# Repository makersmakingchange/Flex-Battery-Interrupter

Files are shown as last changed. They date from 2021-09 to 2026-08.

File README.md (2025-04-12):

# Flex Battery Interrupter

A battery interrupter is a simple, affordable device that enables you to switch adapt many battery powered electronics devices and toys. The battery interrupt is slipped in between the batteries or battery and battery terminal, breaking the circuit until a switch is attached and closed.

This device is a battery interrupter based on a flexible PCB with a mono/stereo 3.5 mm audio jack.

The original design was created by Dale Grover which is called [Flex_Battery_Interrupter_200](https://github.com/makersmakingchange/Flex-Battery-Interrupter/tree/main/Design_Files/PCB_Files/Flex_Battery_Interrupter_200). 

The shorter model was created to offer an even more affordable option which is called [Flex_Battery_Interrupter_100](https://github.com/makersmakingchange/Flex-Battery-Interrupter/tree/main/Design_Files/PCB_Files/Flex_Battery_Interrupter_100).

The difference between the two models is simply the length of the battery interrupter. 

## Makers Making Change Assistive Device Library
 - https://www.makersmakingchange.com/s/product/battery-interrupter-flex-pcb/01tJR000000694IYAQ

## Flex PCB Models

The design files for the two models are available and can be found using following links:

  1. [Flex_Battery_Interrupter_100](https://github.com/makersmakingchange/Flex-Battery-Interrupter/tree/main/Design_Files/PCB_Files/Flex_Battery_Interrupter_100) (100 mm x 34 mm)
  2. [Flex_Battery_Interrupter_200](https://github.com/makersmakingchange/Flex-Battery-Interrupter/tree/main/Design_Files/PCB_Files/Flex_Battery_Interrupter_200) (203.3 mm x 34.3 mm)

## 3D Printed case

[Flex_Battery_Interrupter_Jack_Case](https://github.com/makersmakingchange/Flex-Battery-Interrupter/tree/main/Build_Files/3D_Printing_Files) provides additional support for both Flex PCB and the 3.5mm jack.

## Build 

The following documents will guide you through the build process:

  1. [Flex_Battery_Interrupter_Maker_Checklist](https://github.com/makersmakingchange/Flex-Battery-Interrupter/blob/main/Documentation/V1.0/Flex_Battery_Interrupter_Maker_Checklist.pdf)
  2. [Flex_Battery_Interrupter_Tools_List](https://github.com/makersmakingchange/Flex-Battery-Interrupter/blob/main/Documentation/V1.0/Flex_Battery_Interrupter_Tools_List.pdf)
  3. [Flex_Battery_Interrupter_PCB_Fabrication_Guide](https://github.com/makersmakingchange/Flex-Battery-Interrupter/blob/main/Documentation/V1.0/Flex_Battery_Interrupter_PCB_Fabrication_Guide.pdf)
  4. [Flex_Battery_Interrupter_Assembly_Guide](https://github.com/makersmakingchange/Flex-Battery-Interrupter/blob/main/Documentation/V1.0/Flex_Battery_Interrupter_Assembly_Guide.pdf)

### Gerber Files

The gerber files are available to be sent out to your favorite PCB fabrication company. You can use the following settings when you order your Flex PCBs:

```
Layers: 2 Layers 	
Thickness: 0.2 mm
Min Track/Spacing: 2/2mil
Min Hole Size: 0.15 mm
Finished Copper:1 oz
Stiffener: Without 
3M Tape: without 	
EMI shielding film: without
Board type: Single piece 
```

  1. [Flex_Battery_Interrupter_100](https://github.com/makersmakingchange/Flex-Battery-Interrupter/blob/main/Build_Files/PCB_Files/Gerber_Files/Flex_Battery_Interrupter_100_1.00.zip) (100 mm x 34 mm)
  2. [Flex_Battery_Interrupter_200](https://github.com/makersmakingchange/Flex-Battery-Interrupter/blob/main/Build_Files/PCB_Files/Gerber_Files/Flex_Battery_Interrupter_200_1.01.zip) (203.3 mm x 34.3 mm)

### Components 

The main component of Flex Battery Interrupter is a 3.5mm Stereo Jack which is listed in [Flex_Battery_Interrupter_BOM](https://github.com/makersmakingchange/Flex-Battery-Interrupter/blob/main/Documentation/V1.0/Flex_Battery_Interrupter_BOM_v1.0.csv).

## Attribution
### Contributors
Dale Grover contributed to the inital idea and design of the battery interrupter using a flexible PCB. 

The PCB, 3D printable jack enclosure, and all documentation was completed by Makers Making Change.

## License
Copyright (c) 2022 Neil Squire / Makers Making Change.

This repository describes Open Hardware:
 - Everything needed or used to design, make, test, or prepare the Flex Battery Interrupter is licensed under the [CERN 2.0 Weakly Reciprocal license (CERN-OHL-W)](https://ohwr.org/project/cernohl/wikis/Documents/CERN-OHL-version-2) .
  - Accompanying material such as instruction manuals, videos, and other copyrightable works that are useful but not necessary to design, make, test, or prepare the Ivy Nunchuck Joystick Adapter are published under a [Creative Commons Attribution-ShareAlike 4.0 license (CC BY-SA 4.0)](https://creativecommons.org/licenses/by-sa/4.0/) .

You may redistribute and modify this documentation and make products using it under the terms of the CERN-OHL-W v2 (https:/cern.ch/cern-ohl).
This documentation is distributed WITHOUT ANY EXPRESS OR IMPLIED WARRANTY, INCLUDING OF MERCHANTABILITY, SATISFACTORY QUALITY AND FITNESS FOR A PARTICULAR PURPOSE.
Please see the CERN-OHL-W v2 for applicable conditions.

Source Location: https://github.com/makersmakingchange/Flex-Battery-Interrupter

----

<!-- ABOUT MMC START -->
## About Makers Making Change
[Makers Making Change Logo](https://www.makersmakingchange.com/)

Makers Making Change is a program of [Neil Squire](https://www.neilsquire.ca/), a Canadian non-profit that uses technology, knowledge, and passion to empower people with disabilities.

Makers Making Change leverages the capacity of community based Makers, Disability Professionals and Volunteers to develop and deliver affordable Open Source Assistive Technologies.

 - Website: [www.MakersMakingChange.com](https://www.makersmakingchange.com/)
 - GitHub: [makersmakingchange](https://github.com/makersmakingchange)
 - Bluesky: [@makersmakingchange.bsky.social](https://bsky.app/profile/makersmakingchange.bsky.social)
 - Instagram: [@makersmakingchange](https://www.instagram.com/makersmakingchange)
 - Facebook: [makersmakechange](https://www.facebook.com/makersmakechange)
 - LinkedIn: [Neil Squire Society](https://www.linkedin.com/company/neil-squire-society/)
 - Thingiverse: [makersmakingchange](https://www.thingiverse.com/makersmakingchange/about)
 - Printables: [MakersMakingChange](https://www.printables.com/@MakersMakingChange)

### Contact Us
For technical questions, to get involved, or to share your experience we encourage you to [visit our website](https://www.makersmakingchange.com/) or [contact us](https://www.makersmakingchange.com/s/contact).
<!-- ABOUT MMC END -->

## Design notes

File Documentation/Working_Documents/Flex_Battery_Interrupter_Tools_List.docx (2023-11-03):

Flex Battery Interrupter: Tools List

# Tools

- Soldering iron
- Solder
- Scissors or cutters

Neil Squire, 2021 © 2021 by Neil Squire. Flex Battery Interrupter Tool List is made available under a Creative Commons Attribution-ShareAlike 4.0 License (International): http://creativecommons.org/licenses/by-sa/4.0

Version 1.0 | September 2021 www.MakersMakingChange.com

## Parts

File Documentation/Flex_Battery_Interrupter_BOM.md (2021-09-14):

| Component name                        | Manufacturer                 | MPN                | Digi-Key Part Number    | Unit Cost (CAD)                  | Build Cost (CAD)                 | Link                                                                                                                                                                                                         |
| ------------------------------------- | ---------------------------- | ------------------ | ----------------------- | -------------------------------- | -------------------------------- | ------------------------------------------------------------------------------------------------------------------------------------------------------------------------------------------------------------ |
| 3.5mm Audio Jack (3 Conductor, TRS)   | CUI Devices                  | SJ1-3513           | CP1-3513-ND             |  $                          1.93 |  $                          1.93 | [https://www.digikey.ca/en/products/detail/cui-devices/SJ1-3513/738683](https://www.digikey.ca/en/products/detail/cui-devices/SJ1-3513/738683)                                                                                 |

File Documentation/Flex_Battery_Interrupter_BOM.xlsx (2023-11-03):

Index | Quantity | Digikey Part Number | Manufacturer Part Number | Description | Unit Price (CAD) | Total Price (CAD) | Link
1 | 1 | CP1-3513-ND | SJ1-3513 | CONN JACK STEREO 3.5MM R/A | 1.93 | 1.93 | https://www.digikey.ca/en/products/detail/cui-devices/SJ1-3513/738683
 |  |  |  |  | Total Price: | 1.93

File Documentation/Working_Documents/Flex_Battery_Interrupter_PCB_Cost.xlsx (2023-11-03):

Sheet: 100 mm x 34 mm
Manufacturer | Number of boards | Thickness (mm) | Color | Fabrication fee (US) | Shipping fee (US) | Discount (US) | Other fees (US) | Total with Discount(US) | Unit cost with discount (US) | Total (US) | Unit cost (US)
PCBWay | 5 | 0.2 | Any | 107 | 19 |  |  | 126 | 25.2 | 126 | 25.2
DirtyPCB | 10 | 0.4 | Default | 98.95 |  |  |  | 98.95 | 9.895 | 98.95 | 9.895
PCBGOGO | 10 | 0.2 | Default | 116 | 24 | 25 | 13 | 128 | 12.8 | 153 | 15.3
PCBWay | 10 | 0.2 | Any | 107 | 19 |  |  | 126 | 12.6 | 126 | 12.6
PCBWay | 20 | 0.2 | Any | 131 | 19 |  |  | 150 | 7.5 | 150 | 7.5
PCBWay | 50 | 0.2 | Any | 175 | 19 |  |  | 194 | 3.88 | 194 | 3.88
PCBWay | 75 | 0.2 | Any | 211 | 25 |  |  | 236 | 3.146666667 | 236 | 3.146666667
PCBWay | 100 | 0.2 | Any | 256 | 25 |  |  | 281 | 2.81 | 281 | 2.81
PCBWay | 150 | 0.2 | Any | 311 | 25 |  |  | 336 | 2.24 | 336 | 2.24
PCBWay | 200 | 0.2 | Any | 396 | 32 |  |  | 428 | 2.14 | 428 | 2.14
PCBWay | 250 | 0.2 | Any | 449 | 38 |  |  | 487 | 1.948 | 487 | 1.948

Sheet: 203 mm x 34 mm
Manufacturer | Number of boards | Thickness (mm) | Color | Fabrication fee (US) | Shipping fee (US) | Discount (US) | Other fees (US) | Total with Discount(US) | Unit cost with discount (US) | Total (US) | Unit cost (US)
PCBWay | 5 | 0.2 | Any | 107 | 19 |  |  | 126 | 25.2 | 126 | 25.2
PCBGOGO | 10 | 0.2 | Default | 130 | 24 | 25 | 13 | 142 | 14.2 | 167 | 16.7
PCBWay | 10 | 0.2 | Any | 131 | 19 |  |  | 150 | 15 | 150 | 15
PCBWay | 20 | 0.2 | Any | 175 | 19 |  |  | 194 | 9.7 | 194 | 9.7
PCBWay | 50 | 0.2 | Any | 268 | 25 |  |  | 293 | 5.86 | 293 | 5.86
PCBWay | 75 | 0.2 | Any | 354 | 25 |  |  | 379 | 5.053333333 | 379 | 5.053333333
PCBWay | 100 | 0.2 | Any | 429 | 32 |  |  | 461 | 4.61 | 461 | 4.61
PCBWay | 140 | 0.2 | Any | 575 | 38 |  |  | 613 | 4.378571429 | 613 | 4.378571429

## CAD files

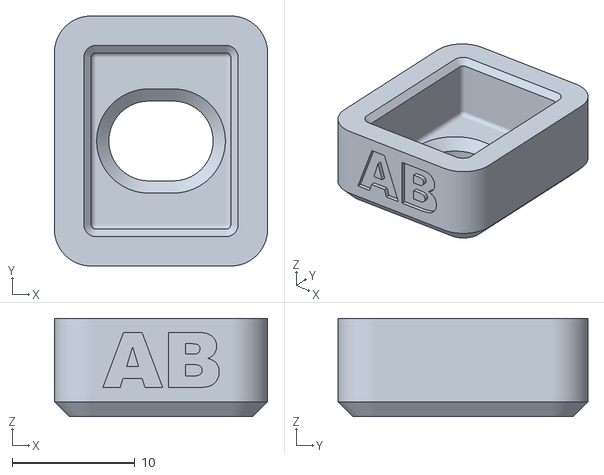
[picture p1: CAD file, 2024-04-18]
Build_Files/3D_Printing_Files/Assembly Tools/Assembly Tool Base.stl
17.4 x 20.4 x 8.00

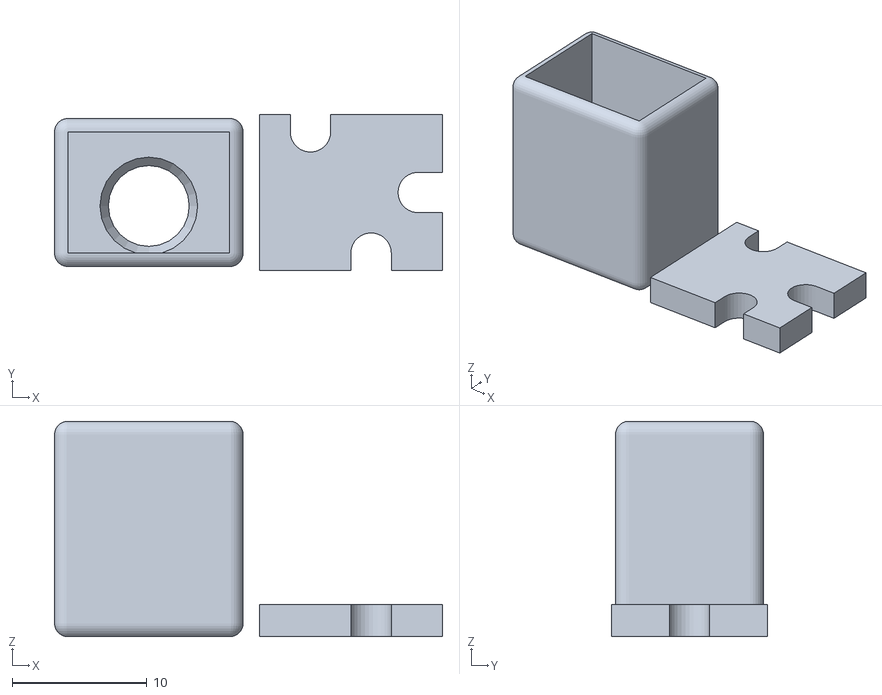
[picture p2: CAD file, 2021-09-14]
Build_Files/3D_Printing_Files/Flex_Battery_Interrupter_Jack_Case_Full_v1.0.stl
28.8 x 11.6 x 16.0

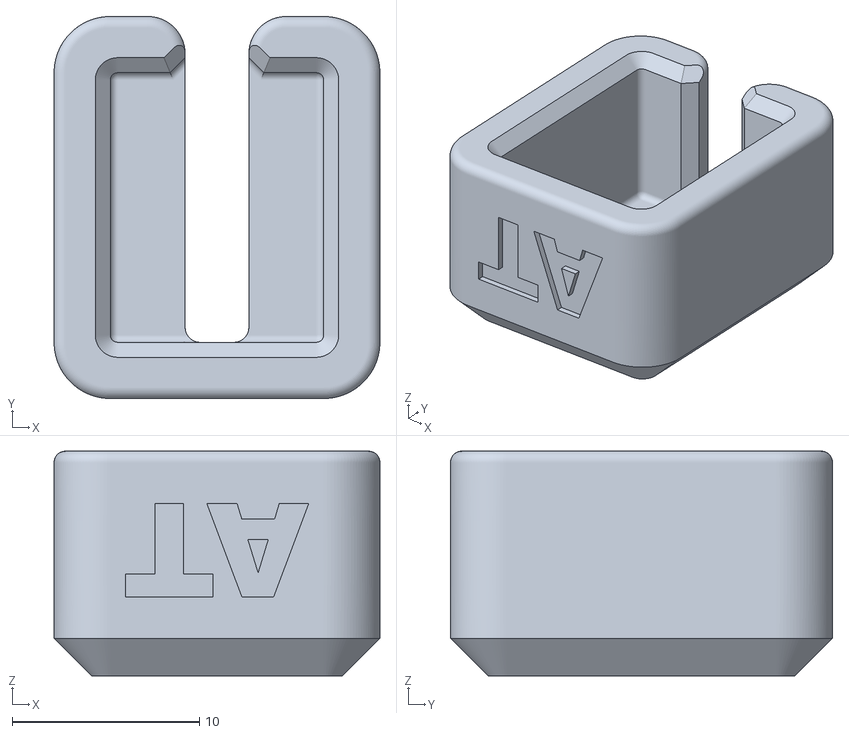
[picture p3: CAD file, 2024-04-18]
Build_Files/3D_Printing_Files/Assembly Tools/Assembly Tool Top.stl
17.4 x 20.4 x 12.0

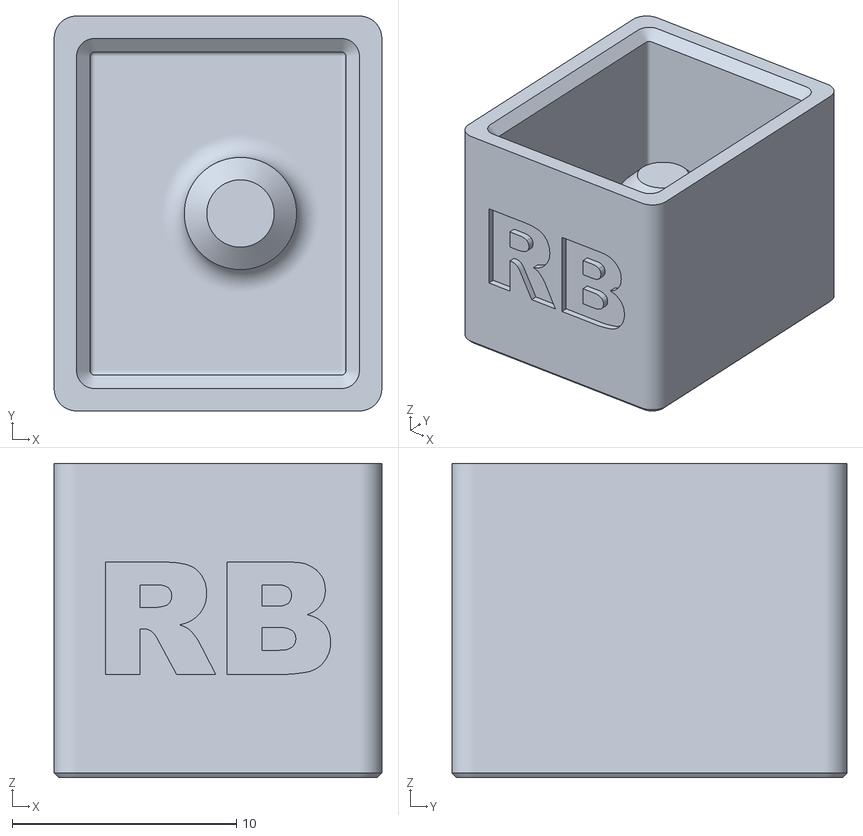
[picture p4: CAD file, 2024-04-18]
Build_Files/3D_Printing_Files/Assembly Tools/Removal Tool Base.stl
14.6 x 17.6 x 14.0

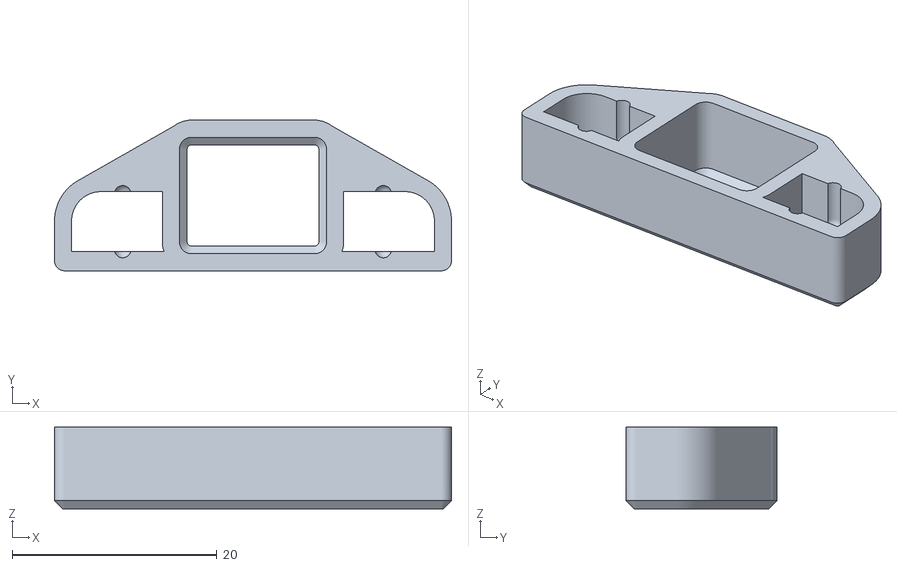
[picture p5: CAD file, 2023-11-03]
Build_Files/3D_Printing_Files/Cable_Tie_Holder/Cable_Tie_Holder_Front.stl
38.8 x 14.7 x 7.99

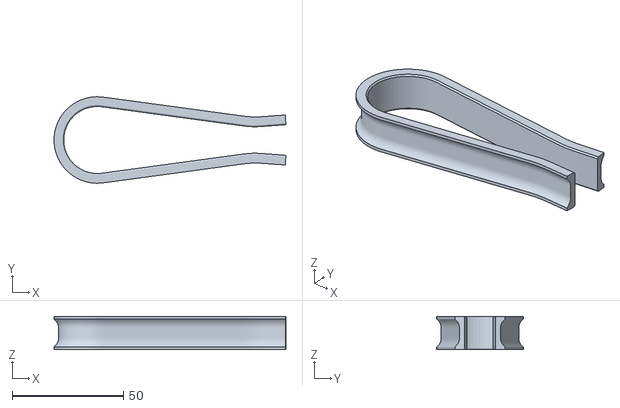
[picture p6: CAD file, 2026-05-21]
Build_Files/3D_Printing_Files/Flex PCB Tester/Flex PCB Tester.stl
104.5 x 39.0 x 15.0

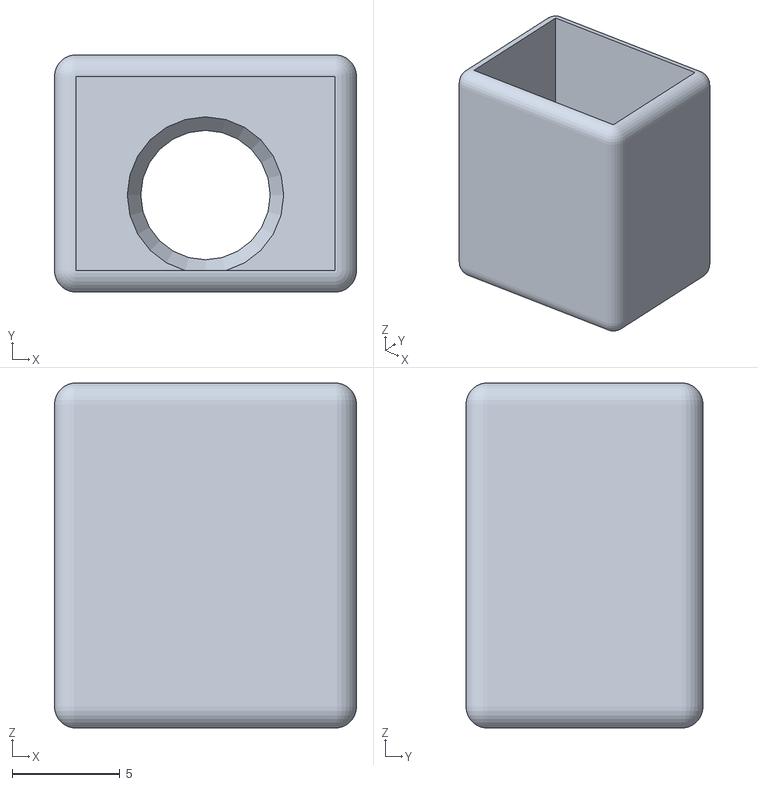
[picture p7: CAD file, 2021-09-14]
Build_Files/3D_Printing_Files/Flex_Battery_Interrupter_Jack_Case_v1.0.stl
14.0 x 11.0 x 16.0

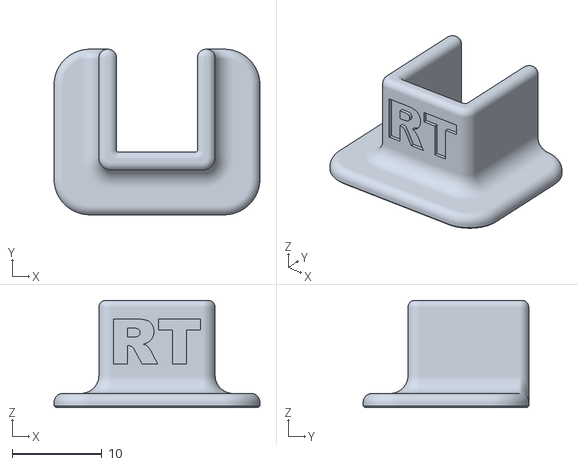
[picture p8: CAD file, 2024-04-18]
Build_Files/3D_Printing_Files/Assembly Tools/Removal Tool Pusher.stl
23.0 x 18.5 x 12.0

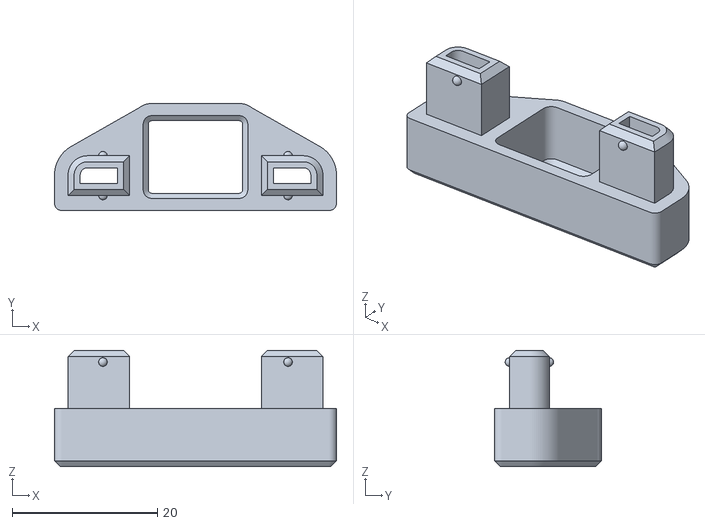
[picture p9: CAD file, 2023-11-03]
Build_Files/3D_Printing_Files/Cable_Tie_Holder/Cable_Tie_Holder_Back.stl
38.8 x 14.7 x 16.0

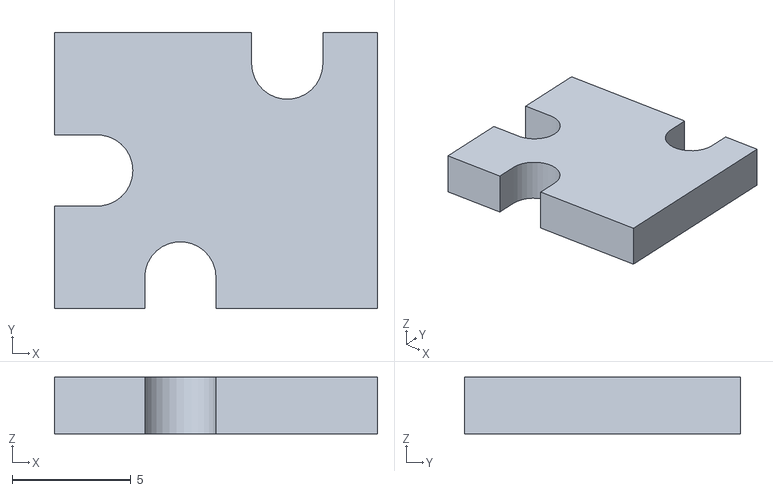
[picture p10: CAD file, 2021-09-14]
Build_Files/3D_Printing_Files/Flex_Battery_Interrupter_Jack_Case_Spacer_v1.0.stl
13.6 x 11.6 x 2.40

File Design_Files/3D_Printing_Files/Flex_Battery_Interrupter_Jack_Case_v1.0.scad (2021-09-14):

 $fn=30;
jackBox();
translate ([15,0,0])jackSabot();



//******************************* SUBROUTINES **********************************

module jackBox(){
translate ([0,0,16/2])difference(){
roundedCube (14,11,16,1);
translate ([0,0,1]) cube([14-2,11-2,16-2], center = true); //remove jack area
translate ([0,-1.0,-16/2])cylinder(d=6,h=3,$fn=24);	 //main jack bore

translate ([0,-1.0,-6.5])cylinder(d1=6,d2=7.5,h=1.5,center = true,$fn=24);	 //jack thread EZ find bevel
}


}//module

module jackSabot(){
translate ([0,0,2.4/2])difference(){
cube([14-.4,12-.4,2.4], center = true);
    hull() { //jack end slot
    translate ([5,0,1])cylinder(d=3,h=8, center = true);//jack end hole
    translate ([5+3,0,1])cylinder(d=3,h=8, center = true);
}//
	
   hull() { //strip end slot
    translate ([-3,4.5,1])cylinder(d=3,h=8, center = true); //strip end hole
    translate ([-3,4+3.5,1])cylinder(d=3,h=8, center = true); //strip end hole
}//

 
  hull() { //middle slot
    translate ([1.5,-4.5,1])cylinder(d=3,h=8, center = true);//middle hole
    translate ([1.5,-4.5-3,1])cylinder(d=3,h=8, center = true);//middle hole
}//
 
}//difference
}//module 


module roundedCube (myBoxWidth,myBoxDepth,myBoxHeight,minkRadius)
//** By Derrick Andrews Same as regular cube, but with rounded sides and bottom
//** maintains proper 'cube' dimensions due to compensation for object expansion 
//** that normally occurs while using Minkowski operations in OpenSCAD)
{
union()
{

minkowski(){
cube([myBoxWidth-minkRadius*2,myBoxDepth-minkRadius*2,myBoxHeight-minkRadius*2], center = true);//Main plate   original cube([90,testSize8,8.5]
sphere(r=minkRadius,$fn=30);
}  //end mink


}//end union
}//end module roundedCube

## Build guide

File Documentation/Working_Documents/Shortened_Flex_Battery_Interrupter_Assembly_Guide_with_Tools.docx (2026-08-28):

Flex Battery Interrupter: Assembly Guide

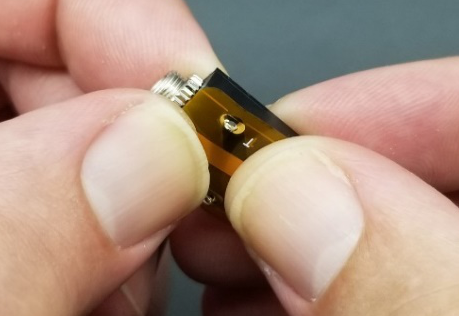
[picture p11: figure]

Step 1: Insert 3.5mm Stereo Jack First insert stereo jack on the Flex PCB side with the thin rectangular part outline, and press the Flex PCB strip onto the stereo jack. Make sure the strip holes remain aligned with the jack pins.

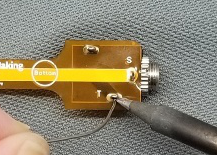
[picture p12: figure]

Step 2: Solder Stereo Jack Joints Solder all three of the stereo jack joints.

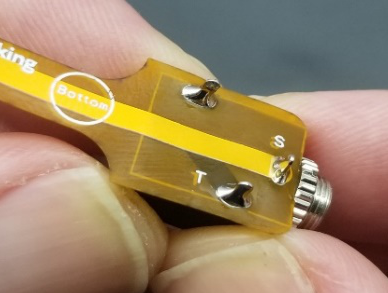
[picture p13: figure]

Step 3: Inspect Soldered Joints Inspect all three solder joints, and make sure they have been properly soldered.
Step 4: Trim Stereo Jack Leads Using flush cutters, trim the excess length off of the leads on the stereo jack.

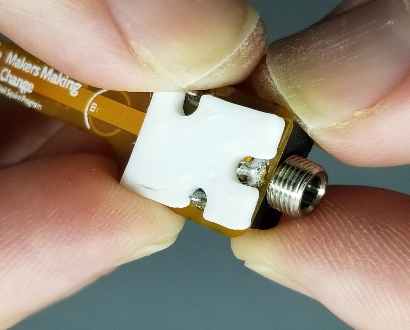
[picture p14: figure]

Step 5: Insert Case Spacer Hold the case spacer against the solder joint side of the Flex PCB strip, as shown. All solder joints should go through the slots, and the spacer should rest flat against the strip. If the spacer can’t rest flat, remove any excess solder from any joint preventing a flat rest.

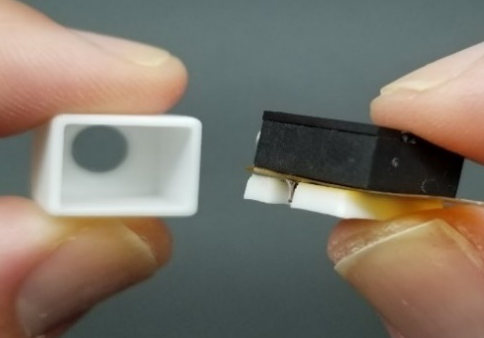
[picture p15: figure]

Step 6: Align Case Spacer Make sure the 3.5mm stereo jack and the case spacer are correctly aligned. The case hole should be on top, and the spacer side of the jack should be on the bottom.

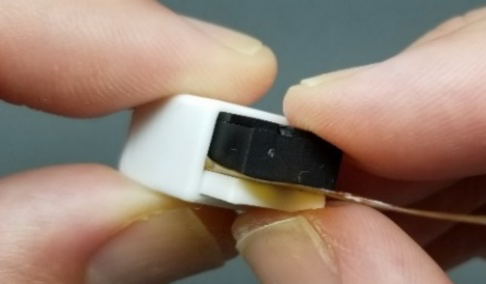
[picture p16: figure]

Step 7: Insert 3.5mm Stereo Jack Slide the aligned 3.5mm stereo jack into the case.

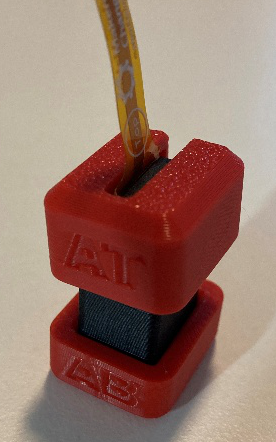
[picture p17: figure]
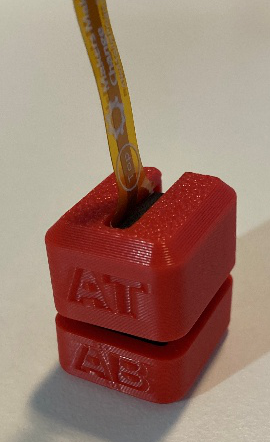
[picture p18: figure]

Step 8 (Optional): Use Assembly Tools to Fully Insert Jack - Place the tool marked “AB” on a flat surface. - Place the partially assembled jack and case into the tool marked “AB”, with the flex PCB facing up and the jack end facing down. - Place the tool marked “AT” on top of the jack, with the flex PCB going through the slot. - Push down on tool “AT” until the jack is all the way in the case.

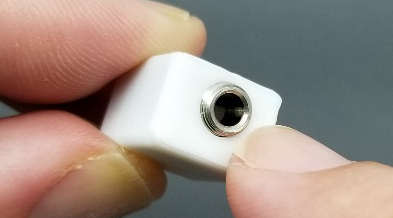
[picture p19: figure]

Step 9: Inspect Insertion of 3.5mm Stereo Jack Make sure the 3.5mm stereo jack is fully inserted, and the jack end protrudes out of the case.

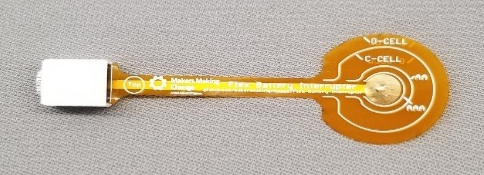
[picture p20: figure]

Step 10: Completion The Flex Battery Interrupter is now fully assembled and is ready for usage. Happy Making!

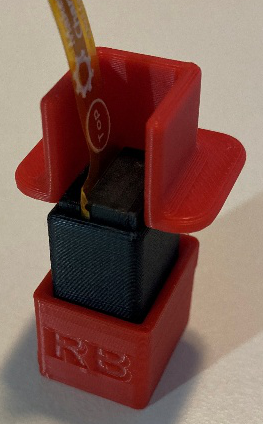
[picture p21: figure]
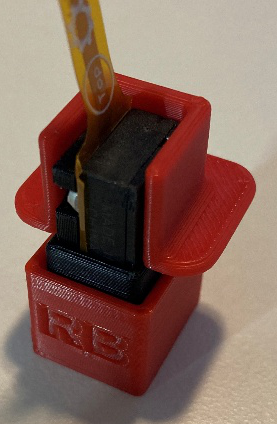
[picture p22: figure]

Troubleshooting If you need to take the battery interrupter out of the case to fix it for any reason, you can use the removal tools. - With tool RB on your work surface, place the jack in the case into tool RB, being careful of the orientation so the hole on the case lines up with the peg in tool RB. - Put tool RT on top of the jack and case, with the tool pressing down on the lip of the case. - Push down on tool RT, the case will slide down and the jack will stay up. - Now remove the case the rest of the way by hand.

Neil Squire, 2026 © 2026 by Neil Squire. Flex Battery Interrupter Quick Guide is made available under a Creative Commons Attribution-ShareAlike 4.0 License (International): http://creativecommons.org/licenses/by-sa/4.0

Version 1.2 | February 2026 www.MakersMakingChange.com

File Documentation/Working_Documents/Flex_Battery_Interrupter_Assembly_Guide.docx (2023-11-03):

Flex Battery Interrupter: Assembly Guide

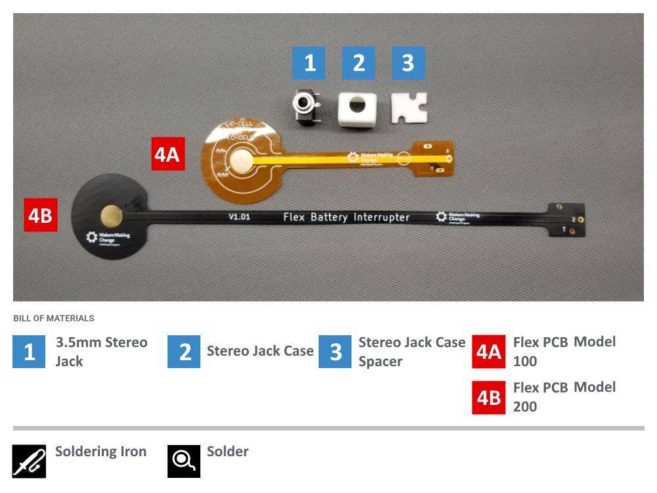
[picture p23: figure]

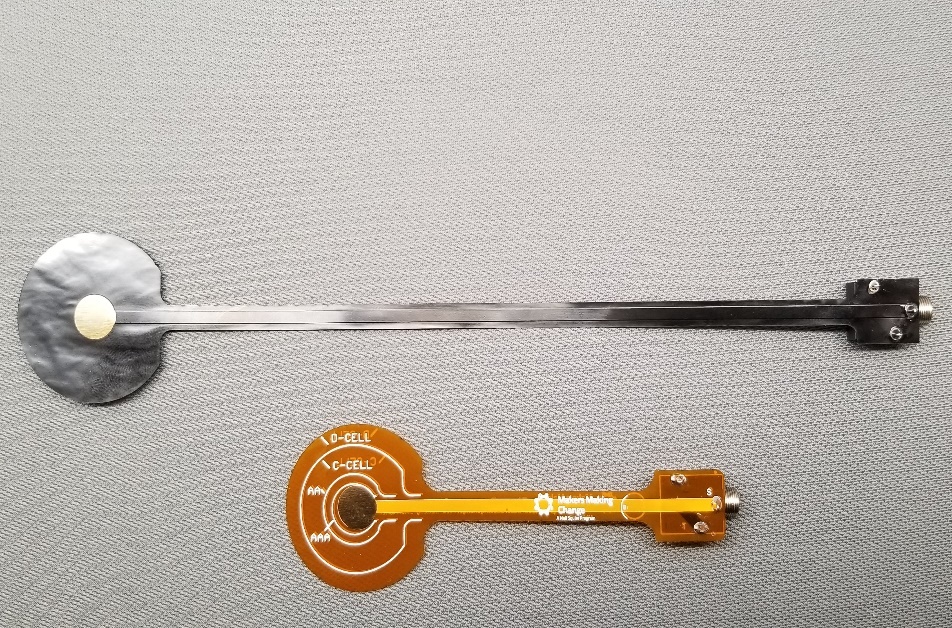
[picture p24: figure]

| Step 1: Flex Battery Interrupter PCB Model The Flex Battery Interrupter is available in two lengths: - Model 100, (100mm or 4”) - Model 200, (200mm or 8”) Please select the model which best fits your needs. As the strip length is the only difference, assembly steps, here for both strip types, is the same.

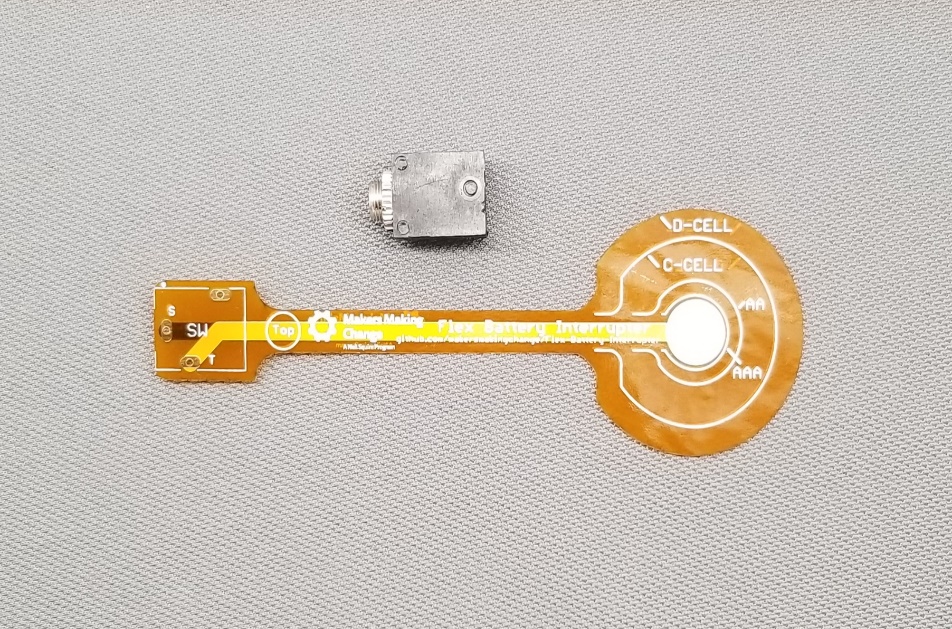
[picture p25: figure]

| Step 2: 3.5mm Stereo Jack Prepare the components including the 3.5mm stereo jack and the flex PCB strip.

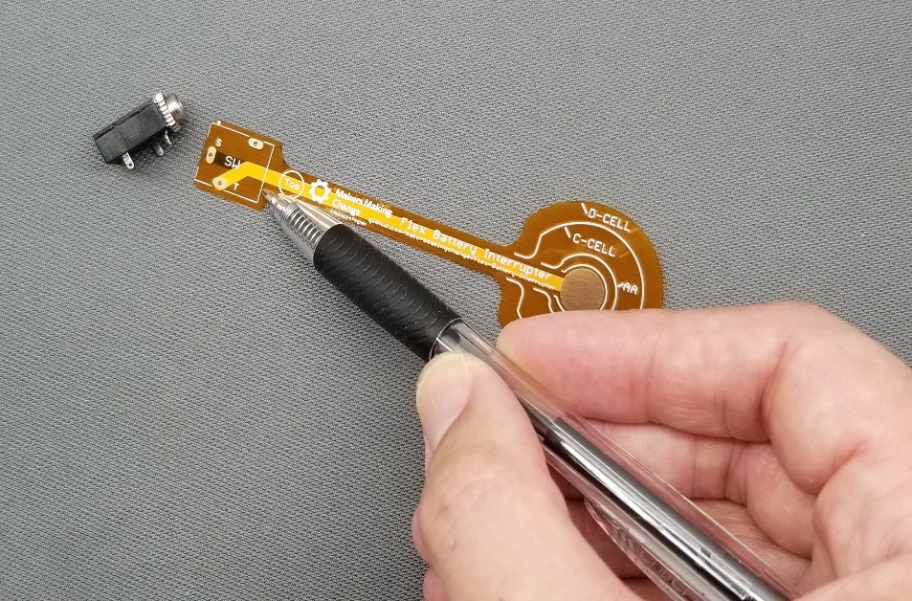
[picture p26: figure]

| Step 3: Solder on the correct PCB side The stereo jack will be inserted on the Flex PCB strip side with a thin rectangular part outline.

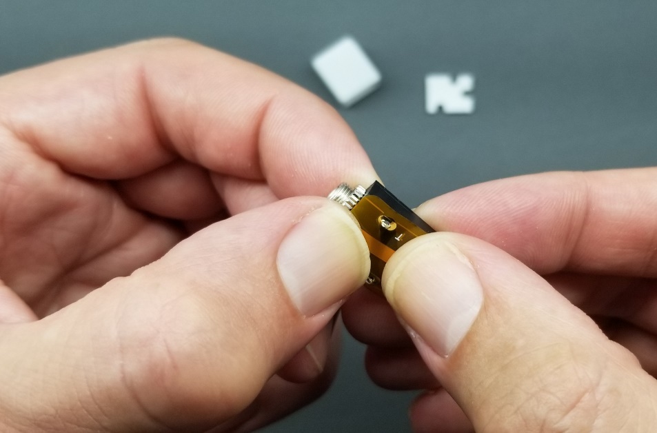
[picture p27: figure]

| Step 4: 3.5mm Stereo Jack Placement First insert stereo jack on the Flex PCB side with the thin rectangular part outline, and press the Flex PCB strip onto the stereo jack. Make sure the strip holes remain aligned with the jack pins, as you do so.

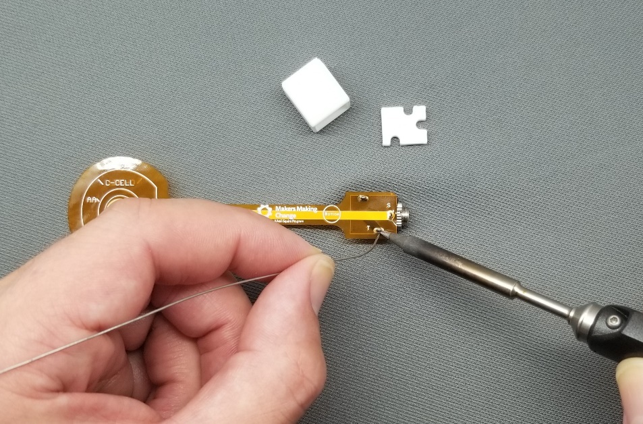
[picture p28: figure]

| Step 5: Solder Stereo Jack Joints Solder all three of the stereo jack joints.

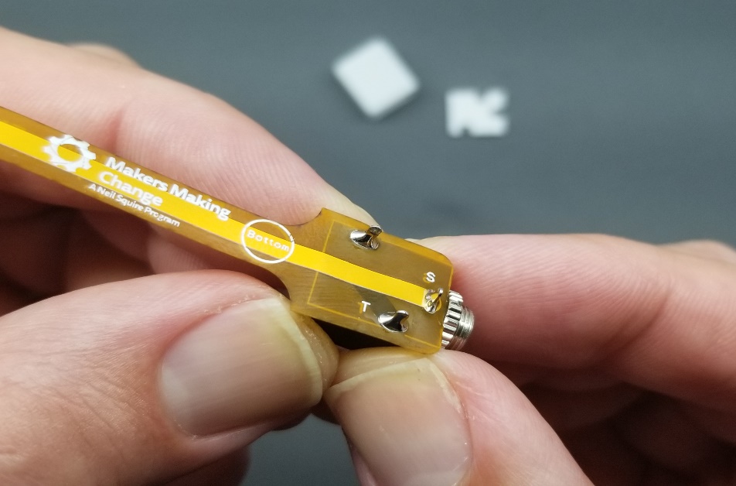
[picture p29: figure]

| Step 6: Inspect Soldered Joints Inspect all three solder joints, and make sure they have been properly soldered.

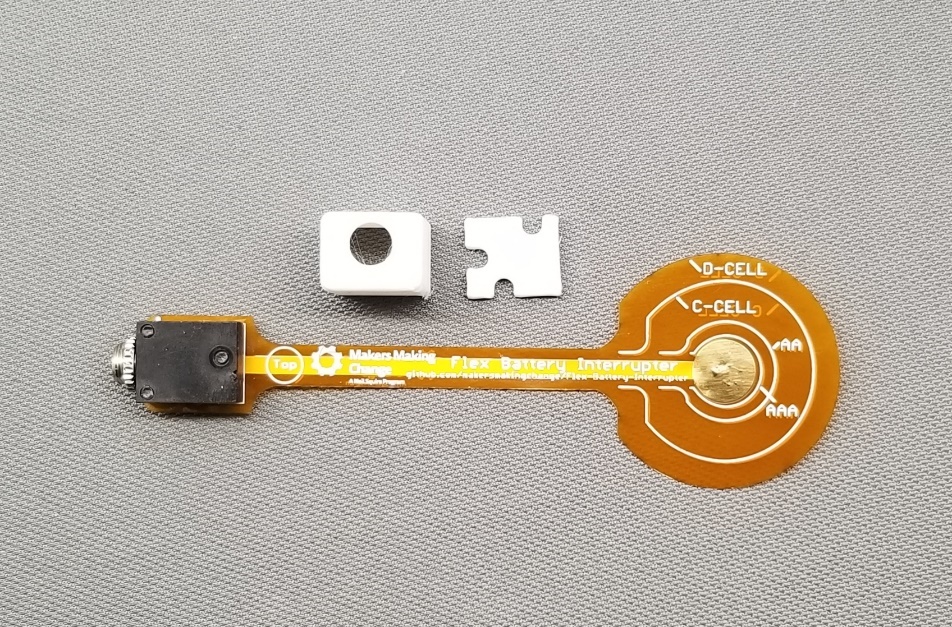
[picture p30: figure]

| Step 7: Alignment Pre-Check The pieces in the photo need to be assembled together in the correct orientation. Note that the hole in the case is closer to the top (jack) side, and the end slot in the jig saw shaped piece will go to the connector jack end.

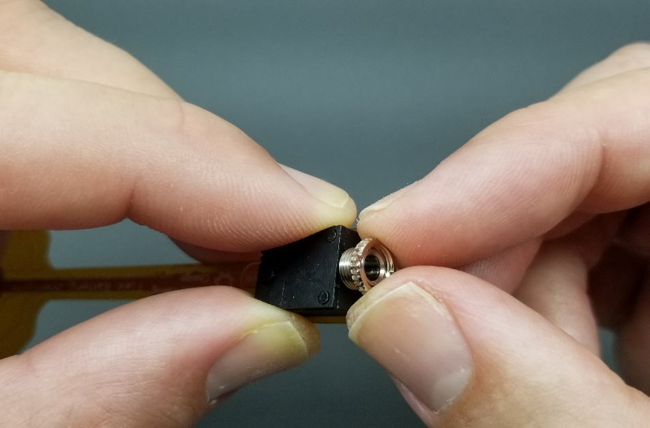
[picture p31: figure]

| Step 8: Remove Retainer Ring Remove the 3.5mm stereo jack retainer ring by turning it counter-clockwise, until it comes off.

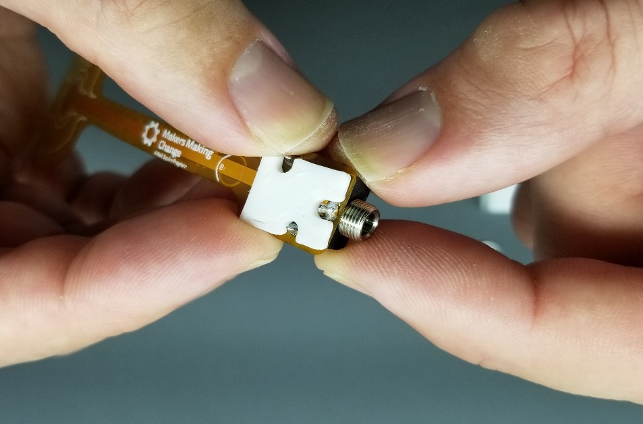
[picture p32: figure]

| Step 9: Insert Case Spacer Hold the case spacer against the solder joint side of the Flex PCB strip, as shown. All solder joints should go through the slots, and the spacer should rest flat against the strip. If the spacer can’t rest flat, remove any excess solder from any joint preventing a flat rest.

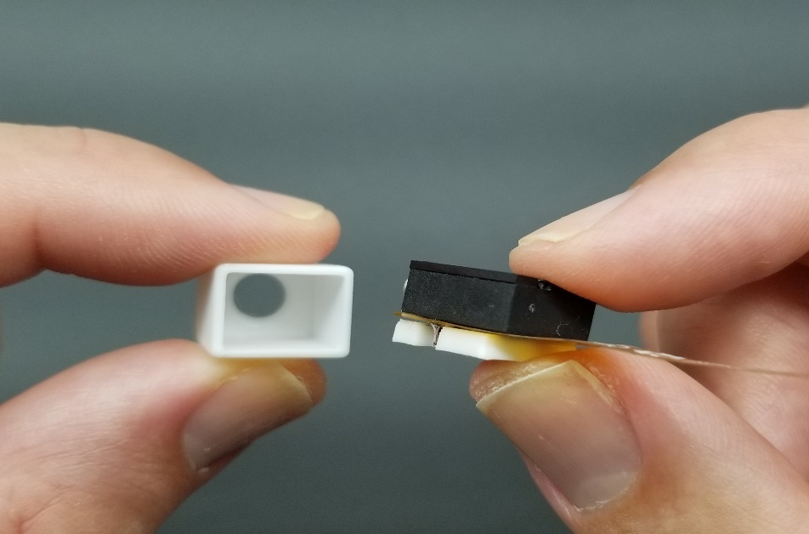
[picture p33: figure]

| Step 10: Align Case Spacer Make sure the 3.5mm stereo jack and the case spacer are correctly aligned. The case hole should be on top, and the spacer side of the jack should be on the bottom.

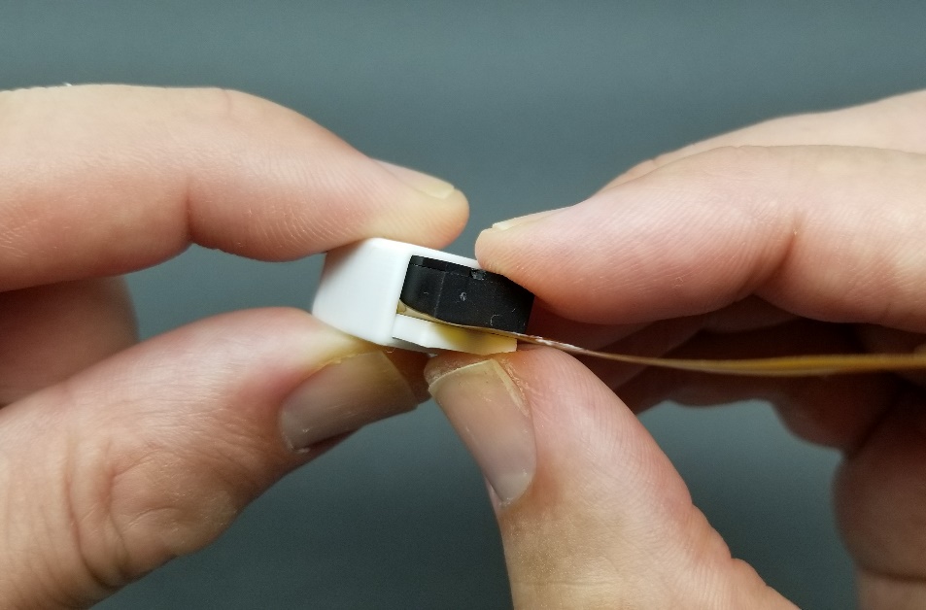
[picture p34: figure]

| Step 11: Insert 3.5mm Stereo Jack Slide the aligned 3.5mm stereo jack fully into the case.

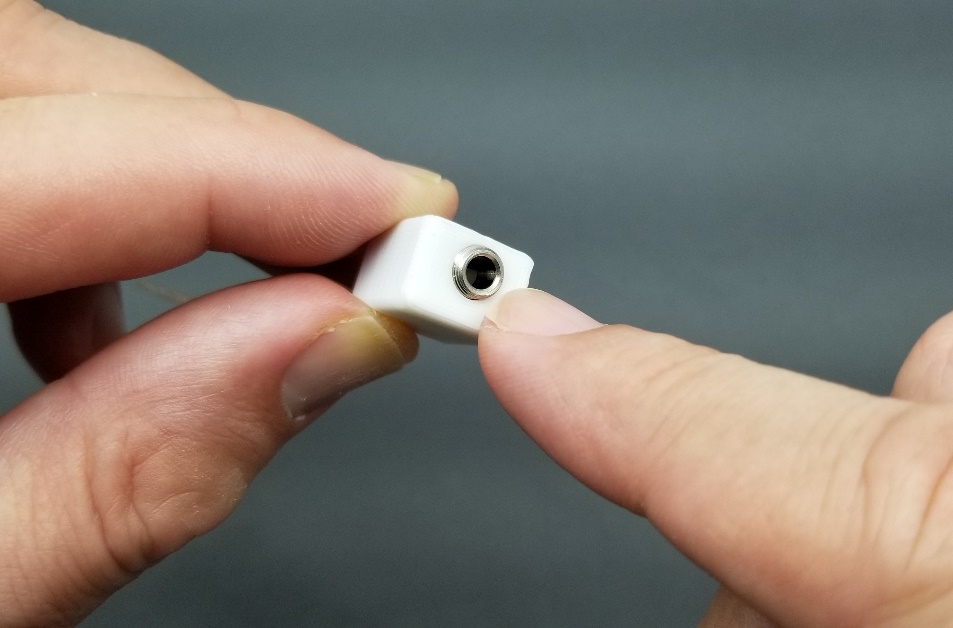
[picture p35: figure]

| Step 12: Inspect Insertion of 3.5mm Stereo Jack Make sure the 3.5mm stereo jack is fully inserted, and the jack end protrudes enough for the retainer ring to be inserted.

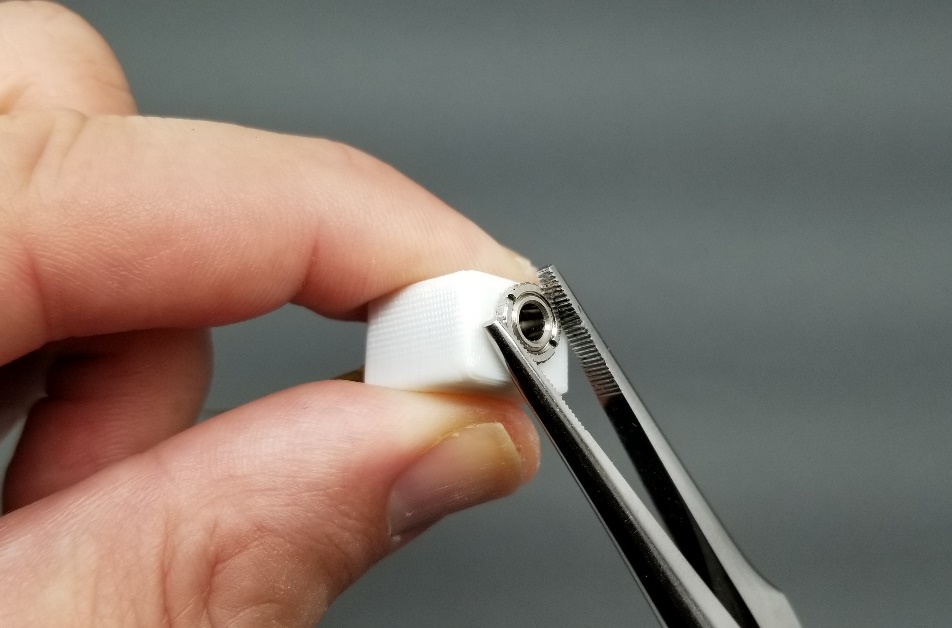
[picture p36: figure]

| Step 13: Insert 3.5mm Stereo Jack Retainer Ring Insert the 3.5mm stereo jack retainer ring, by screwing it on clockwise. This will secure the case. If you have large fingers, it may be easier to tighten the retainer with a pair of fine tipped pliers (as shown).

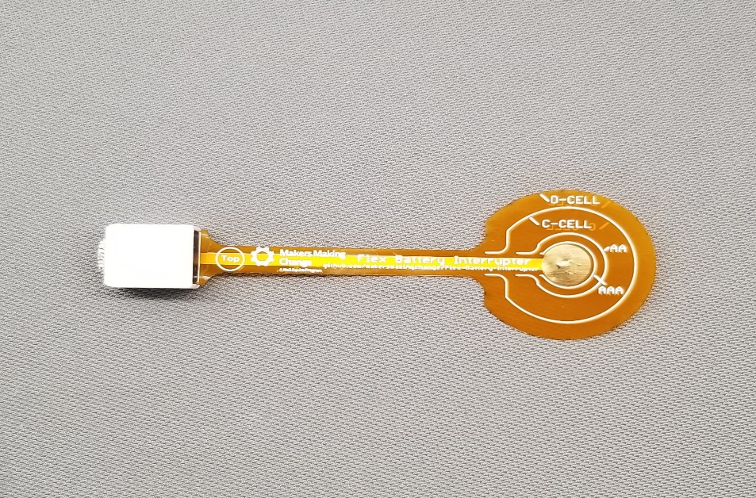
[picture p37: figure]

| Step 14: Completion The Flex Battery Interrupter is now fully assembled and is ready for usage. Happy Making!

Neil Squire, 2021 © 2021 by Neil Squire. Flex Battery Interrupter Quick Guide is made available under a Creative Commons Attribution-ShareAlike 4.0 License (International): http://creativecommons.org/licenses/by-sa/4.0

Version 1.0 | September 2021 www.MakersMakingChange.com

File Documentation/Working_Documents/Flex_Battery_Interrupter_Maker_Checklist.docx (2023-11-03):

## Maker To Do List

Flex Battery Interrupter - Maker Checklist

☐ Build the Flex Battery Interrupter

☐ 3D print the battery interrupter case and case spacer

# Items to Give to User

☐ Flex Battery Interrupter

☐ Flex Battery Interrupter: User Guide

Neil Squire, 2021 © 2021 by Neil Squire. Flex Battery Interrupter Checklist is made available under a Creative Commons Attribution-ShareAlike 4.0 License (International): http://creativecommons.org/licenses/by-sa/4.0

Version 1.0 | September 2021 www.MakersMakingChange.com

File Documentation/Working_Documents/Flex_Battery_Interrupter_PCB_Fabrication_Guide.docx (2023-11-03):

## Flex Battery Interrupter PCB Fabrication Guide

Version 1.0

# 1. Introduction

## 1.1. What is PCB?

PCB (Printed circuit board) is a board that has lines and pads that connect various points together. The board includes traces that electrically connect the various connectors and components to each other. A PCB allows signals and power to be routed between physical devices. Solder is the metal that makes the electrical connections between the surface of the PCB and the electronic components. [1]

## 1.2. What is PCB Fabrication?

PCB fabrication is the assembly method for circuit boards used in electronic devices. The layers of the board are put together along with the specific surface pattern based on the design files that is used in electronics manufacturing.[2]

## 1.3. What is a Gerber file?

Users create their own files for manufacturing based on the design files and send them to the manufacturer. The design files for manufacturing PCB are converted to a standard format known as a Gerber file. This is an industry standard for recording the specification of a PCB.[2]

# 2. PCB design tools

There are many different tools for designing PCB’s and you can select any of the available tools based on your previous experience or the requirements of your design. The process of designing PCB is not in the scope of this document but you can find courses or books that can help you understand the process of designing electronics circuits and PCB’s.

Here are the most common PCB design tools:

- Altium Designer (https://www.altium.com/) : Paid with Free Trial and student license.
- Eagle (https://www.autodesk.ca/en/products/eagle/) : Free limited version includes 2 schematic sheets, 2 signal layers, and an 80cm2 (12.4in2) board area.
- Kicad (https://www.kicad-pcb.org/) : Opensource with GNU’s GPL copyright agreement.
- Fritzing (https://fritzing.org) : Opensource version available on github and the paid application is available. Limited options suitable for basic designs.
- Upverter (https://upverter.com/) : Free cloud-based design tool. It requires sign up for usage.

There are other available tools that can be used to design PCBs.

# 3. How to generate PCB gerber files for fabrication?

Once the PCB board file is created using your favorite PCB design tool then you can generate gerber files which is used by PCB fabrication companies to fabricate your design. The CAM processing tool uses the gerber generator file to create gerber files. The gerber generator file is usually provided by PCB fabrication company of your choice or can be created based on gerber files format which can be found on the website of the PCB fabrication company.

Each PCB board file includes different top and bottom layers and gerber files provide specifications for each of these layers by combining layers together based on the format specified by gerber file generator.

Common layers:

- Top & Bottom Copper
- Top & Bottom Silkscreen
- Top & Bottom Soldermask
- Drill
- Drill Station Info
- Photoplotter Info
- Mill Layer
- Top Paste

There is no standard format for the gerber file generator and there are variations of formats used by PCB fabrication companies.

You can find the final generated gerber files of the projects involving PCB designs for common PCB fabrication companies on our website. You can use the generated gerber files available if you are using one of the fabrication companies listed below or you can create your own gerber files based on PCB design files.

- Seeed Fusion PCB (https://www.seeedstudio.com/fusion.html)
- PCBWay (https://www.pcbway.com)
- OSH Park ~ (https://oshpark.com/)
- JLCPCB (https://jlcpcb.com)

We now go over process of generating gerber files using three common PCB design tools.

## EAGLE

1. Open the board file of your PCB design using Eagle
2. Select File > CAM Processor
3. Click on “Load job file” dropdown menu button and select “Open CAM file”
4. Download or create the gerber generator file (.cam) used by your PCB fabrication company of your choice
5. Navigate in your system and find the directory that includes the gerber file generator file with. cam extension
6. Select the gerber file generator file and click on “Open” button
7. Double check the Output file layers on left menu bar to make sure there are no layers are missing
8. Click on “Process Job” button
9. Select the output directory (Create a new directory called “gerbers” as an example)
10. The process of creating the gerber file will start and finish once you receive a popup message indicating that “Job Proceed Successfully!”
11. Click on “OK” button
12. Navigate to the directory that includes the generated gerber files (“gerbers” directory as an example)
13. Select all the gerber/drill files in the directory that saved them and generate a compressed file in Zip format.
14. You can now submit the compressed Zip file that includes the gerber files to the PCB fabrication company of your choice.

## Kicad

1. Open the board file of your design file using Kicad. [4]
2. Select File > Plot
3. Check the layers in “Plot” window for creating gerber files according to fabrication company instructions.
  - Check following layers: Top Copper (F.Cu), Soldermask (F.Mask), Silkscreen (F.SilkS), Bottom Copper (B.Cu), Soldermask (B.Mask), Silkscreen (B.SilkS), Board outline (Edge.Cuts)
4. Set the “Output directory” to save the generated gerber files. You can also use “Browse…” button to set the path to the directory.
5. Uncheck “Plot sheet reference on all layers” option.
6. Uncheck “Plot footprint values” option.
7. Check “Exclude PCB edge layer from other layers” option.
8. Check “Use Protel filename extensions” option.
9. Click on “Plot” button to generate and save gerber files in the specified output directory to save gerber files.
10. Next, configure the settings to generate drill file
11. Click on “Generate Drill File” button.
12. Set the “Output directory” to save the generated drill file. You can also use “Browse…” button to set the path to the directory. Use the same output directory as you selected to save the gerber files.
13. Check “Inches” as drill units.
14. Check “Decimal Format” as zeros format.
15. Check “PostScript” as drill map file format.
16. Check the “Merge PTH and NPTH holes into one file” option
17. Click on “Drill File” or press “Enter” to generate the drill file.
18. Click on “Close” to close “Drill Files Generation” Window.
19. Click on “Close” again to close “Plot” Window.
20. Verify the generated gerber files using a gerber viewer tool to make sure that all layers have been generated correctly.
21. Select all the gerber/drill files in the directory that saved them and generate a compressed file in Zip format.
22. You can now submit the compressed Zip file that includes the gerber files to the PCB fabrication company of your choice.

# 4. How to check and confirm PCB Gerber files?

It is recommended to double check or triple check the final generated gerber files of your design to make sure there are no issues with process of gerber files generation. The PCB fabrication companies mostly provide online gerber file viewer tools that you can use to confirm your design once you upload your gerber files compressed as a Zip file. However, you can use other gerber file viewer to check your design files before submitting the gerber files.

The following gerber viewer tools are recommended:

- Online Gerber Viewer (https://www.gerber-viewer.com/)
- gerbv (https://sourceforge.net/projects/gerbv/)

Select all the generated gerber file layers in the “gerbers” directory and view them to make sure all the layers are aligned.

# 5. What is a Flex PCB?

A Flex PCB is a patterned arrangement of printed circuitry that utilizes flexible based material with or without flexible coverlay. coverlay is a two part sheet of polyimide that is used to protect the external circuitry of a flexible circuit board. The flexible component assembly can be fabricated using the same components used for rigid printed circuit boards, but the flexible material allows the board to conform to a desired shape during its application.

# 6. Where to send PCB gerber files for fabrication?

The process to send the gerber files for fabrication may differ from company to company but there are general steps you can follow to send your gerber files for fabrication.

1. Select the fabrication company (Here are our recommended fabrication companies)
  - Seeed Fusion PCB
  - PCBWay
  - OSH Park ~
  - PCBgogo
2. Create an account on PCB fabrication website or use temporary login if it is available
3. Select the fabrication service
4. Upload the compressed Zip file that includes your gerber files
5. Select the available options based on your design requirements. The standard options for most of our projects:
- PCB Layers: 2 Layers
- PCB dimensions should update based on your uploaded gerber files, but you can manually entry the dimensions as well
- PCB quantity can vary based on your requirements (Minimum 5)
- PCB Color can be changed if the fabrication company offers the option. The default option has the fastest turnaround time.
- PCB Type: Polyimide Flex
- FPC Thickness: 0.2mm
- Min Hole Size: 0.15 mm
- Min Track/Spacing: 2/2mil
- Finished Copper:1 oz
- Stiffener: Without
- 3M Tape: without
- EMI shielding film: without
- Board type: Single piece
- Surface Finish
- Other parameters don’t need to be changed. You can use the default values.
6. Check the uploaded gerber files using online gerber viewer tool if it is offered by the fabrication company and make sure there are no issues.
7. Add the uploaded design to the order
8. Add another design if you are doing multiple orders
9. Proceed to the checkout and enter your billing and shipment information
10. Select the shipping method
11. Submit your order for production
12. The technician will contact you for additional information or corrected files if there are issues with your design files.
13. You will receive an email when your design goes to production
14. You will receive another email once your PCBs are produced and shipped

This includes the instructions for fabrication of PCB designs based on generated gerber files.

# Reference

1. https://learn.sparkfun.com/tutorials/pcb-basics/all
2. https://www.hi5electronics.co.uk/what-is-pcb-fabrication/
3. https://support.jlcpcb.com/article/42-how-to-export-altium-pcb-to-gerber-files
4. https://support.jlcpcb.com/article/44-how-to-export-kicad-pcb-to-gerber-files

Neil Squire, 2021 © 2021 by Neil Squire. Flex Battery Interrupter Quick Guide is made available under a Creative Commons Attribution-ShareAlike 4.0 License (International): http://creativecommons.org/licenses/by-sa/4.0

Version 1.0 | September 2021 www.MakersMakingChange.com

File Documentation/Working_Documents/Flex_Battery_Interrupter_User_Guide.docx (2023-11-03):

Flex Battery Interrupter: Quick Guide

# Introduction

The flex battery interrupter is a simple, affordable device that enables you to switch adapt many battery-powered devices and toys. The battery interrupter is slipped in between the batteries or battery and battery terminal. This breaks the circuit (turning it off) until an external switch is attached and activated.

This device is a battery interrupter based on a flexible PCB with a mono/stereo 3.5mm audio jack.

# Features

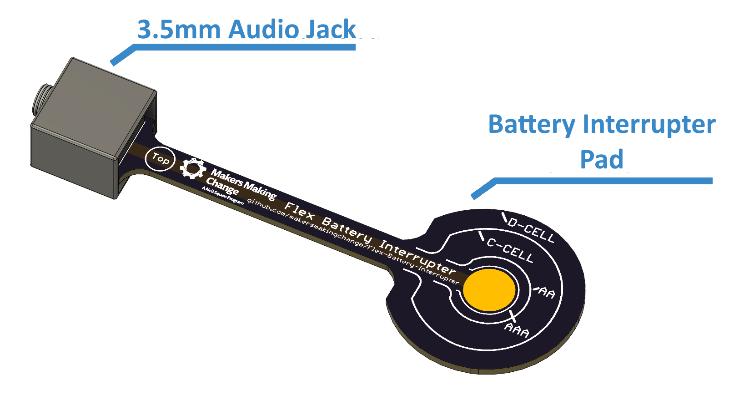
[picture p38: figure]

# Caution

The Plasma Globe used for demonstration in this guide is not a toy, and should only be used under adult supervision.

# Usage

1. Remove end battery positive terminal end.

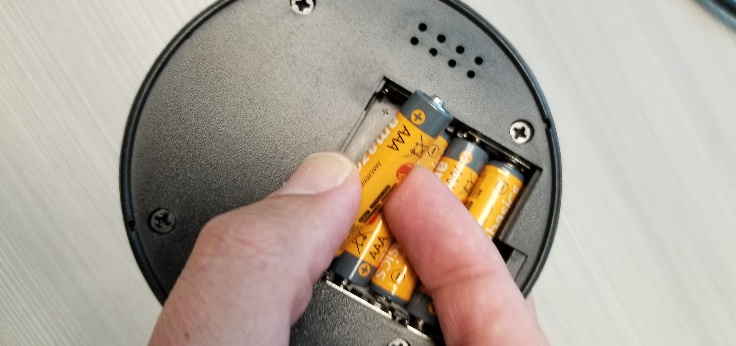
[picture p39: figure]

2. Insert trimmed strip end against positive battery terminal.

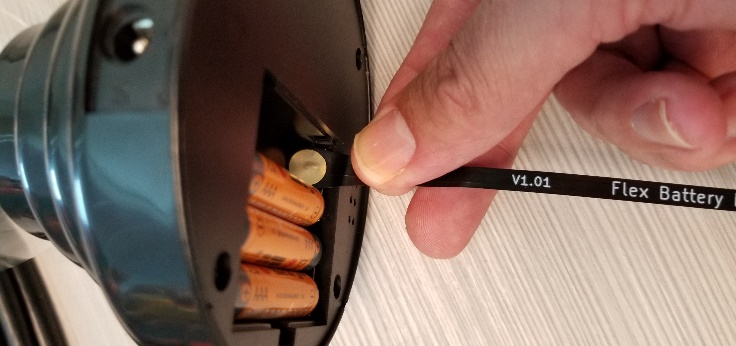
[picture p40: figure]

3. Return battery tip end back into case, to hold the strip in place.

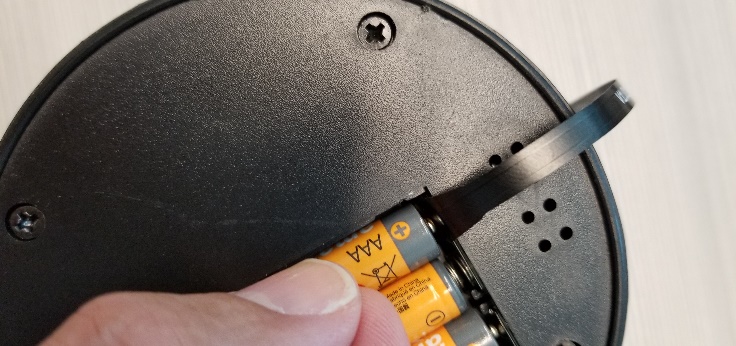
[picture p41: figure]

4. Return Battery cover.

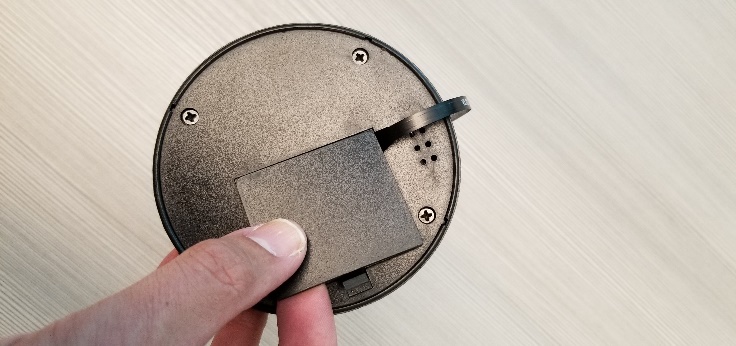
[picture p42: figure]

5. The modification is complete.

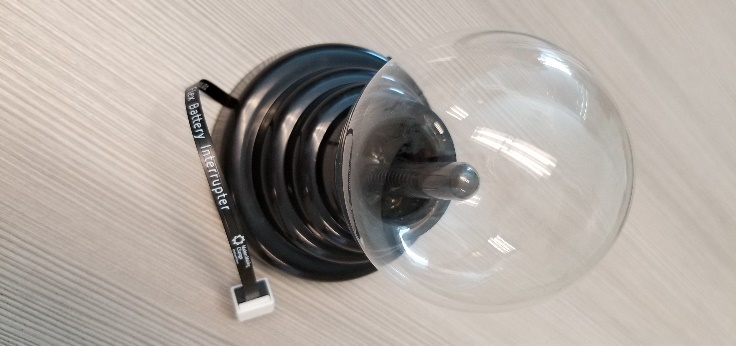
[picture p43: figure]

6. Insert a switch with 3.5mm plug into the completed jack end.

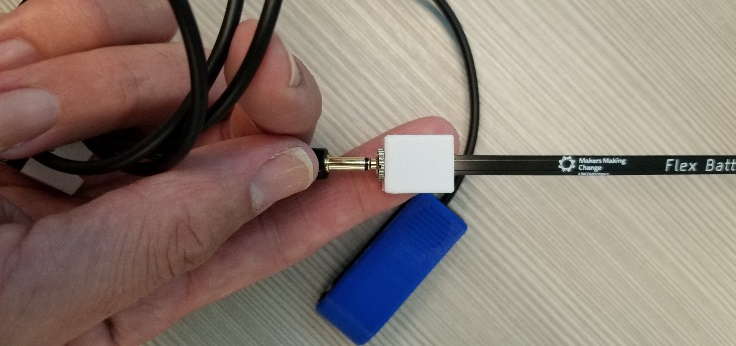
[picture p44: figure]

7. If the device has an on/off switch turn it on. If the battery interrupter is working, the device should not turn on with using the switch connected to the strip.

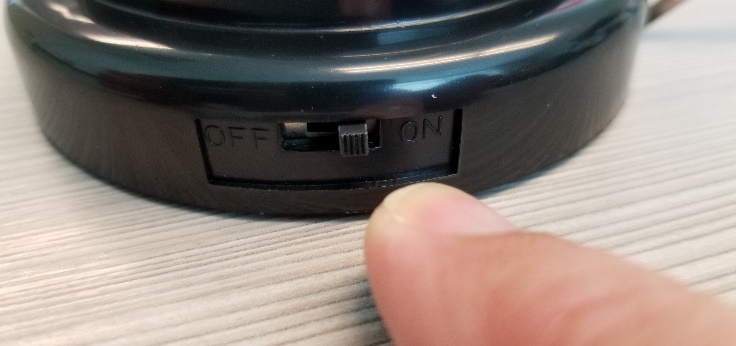
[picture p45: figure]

8. Activate the plugged-in switch, the device should turn on.

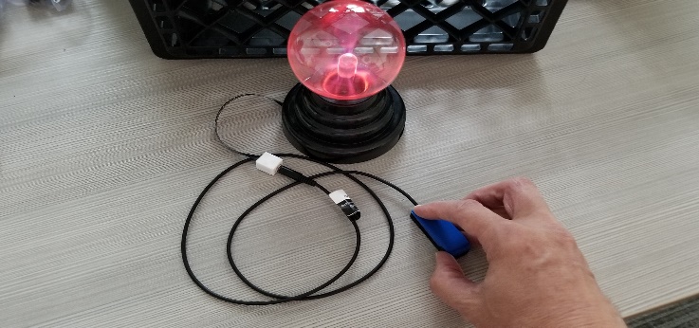
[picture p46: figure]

# Specification

Specification | Details
Size | 100 mm x 34 mm x 6.2 mm (Model 100) 203.3 mm x 34.3 mm x 6.2 mm (Model 200)
Supported Batteries | D-Cell, C-Cell, AA, AAA

Neil Squire, 2021 © 2021 by Neil Squire. Flex Battery Interrupter Quick Guide is made available under a Creative Commons Attribution-ShareAlike 4.0 License (International): http://creativecommons.org/licenses/by-sa/4.0

Version 1.0 | September 2021 www.MakersMakingChange.com

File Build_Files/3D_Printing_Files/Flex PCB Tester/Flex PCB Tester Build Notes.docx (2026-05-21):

# Flex PCB Tester - Build Notes

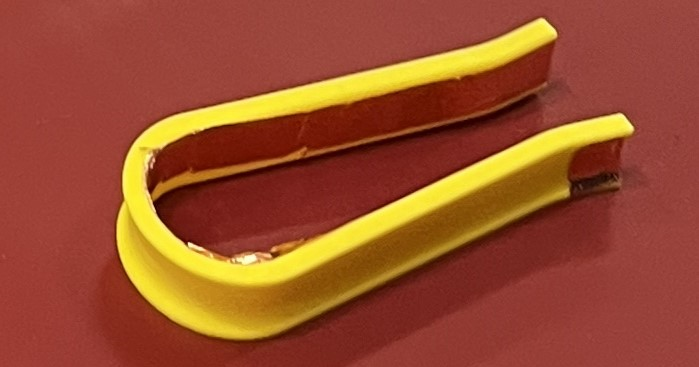
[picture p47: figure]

1. Print
2. Wrap it in copper tape from the contacts (where you pinch it together), and all the way around the inside of the horseshoe.
  a. Optional: You can start / finish on the outside ends of the external channel (where you hold it) to help prevent the copper tape from peeling up during use.
3. Make sure the copper tape is continuous / no breaks anywhere.
4. To Test / Use:
  - Plug the Flex PCB into a Battery Tester
  - Pinch the center contact of the FlexPCB (the switch tester should light up)
    - You might need to fiddle with it a bit until you get the hang of it

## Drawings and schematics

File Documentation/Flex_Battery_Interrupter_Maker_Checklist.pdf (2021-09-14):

# Maker To Do List

## ☐ Build the Flex Battery Interrupter

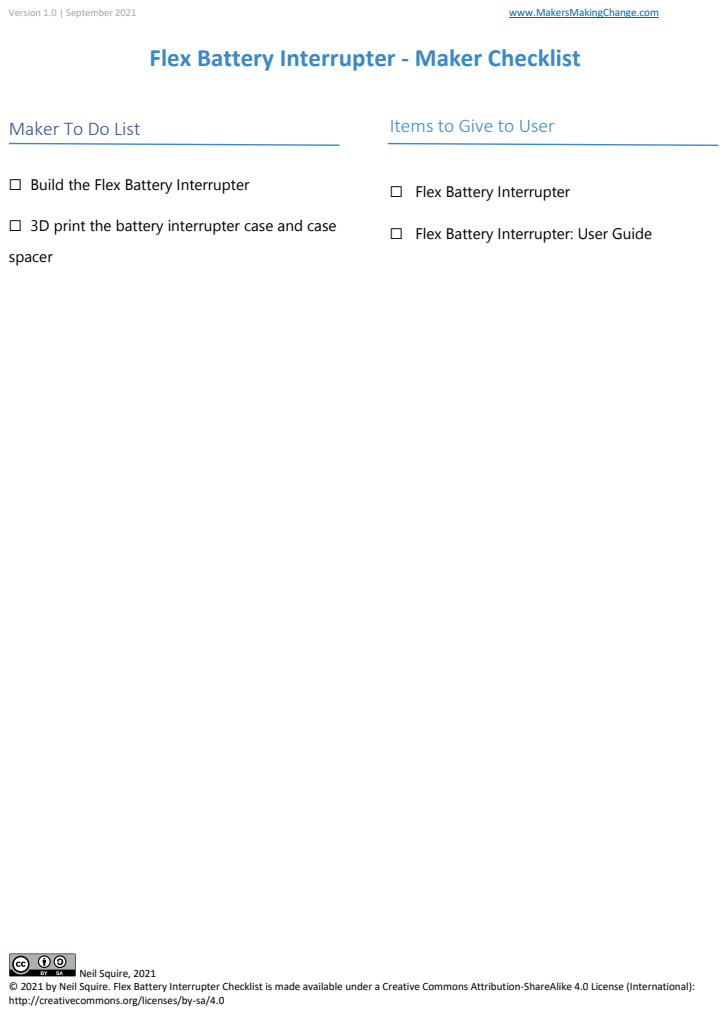
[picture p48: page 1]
Version 1.0 | September 2021; www.MakersMakingChange.com; Neil Squire, 2021; spacer

Flex Battery Interrupter - Maker Checklist

Items to Give to User

☐ Flex Battery Interrupter

☐ 3D print the battery interrupter case and case

☐ Flex Battery Interrupter: User Guide

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

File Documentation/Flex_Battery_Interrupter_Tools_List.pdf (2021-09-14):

# Flex Battery Interrupter: Tools List

# Tools

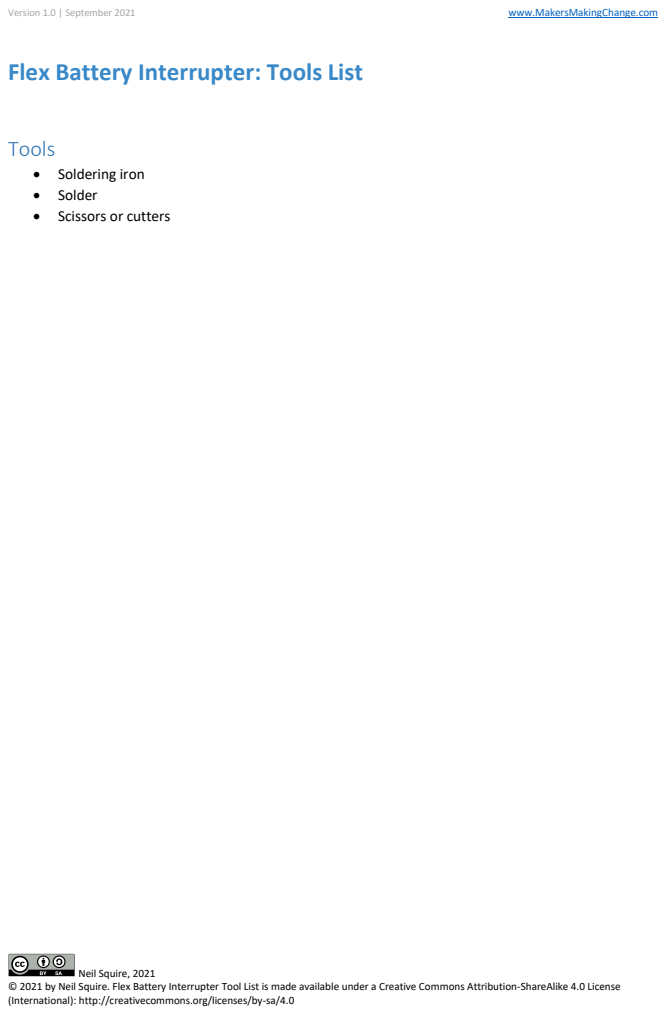
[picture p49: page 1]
Version 1.0 | September 2021; www.MakersMakingChange.com; Neil Squire, 2021

• Soldering iron
• Solder
• Scissors or cutters

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

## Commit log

2020-12-25 Created 10cm version of the interrupter
    [Flex_Battery_Interrupter.brd, Flex_Battery_Interrupter.sch]
2020-12-25 Created gerber files
    [Flex_Battery_Interrupter.GBL, Flex_Battery_Interrupter.GBO, Flex_Battery_Interrupter.GBP, Flex_Battery_Interrupter.GBS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]
2020-12-25 Added BOM file
    [Flex_Battery_Interrupter_BOM.csv, Flex_Battery_Interrupter_BOM.xlsx]
2021-01-08 Removed ground plane of PCB
    [Flex_Battery_Interrupter.GBL, Flex_Battery_Interrupter.brd, drills_1_16.xln, gerber_job.gbrjob]
2021-01-16 Added pcb cost from 3 different fabrication companies
    [Flex_Battery_Interrupter_PCB_Cost.xlsx]
2021-04-21 Renamed the Flex Battery Interrupter to Flex Battery Interrupter 100 (100mm). Model:100,Version:1.00
    [Flex_Battery_Interrupter.GBL, Flex_Battery_Interrupter.GBO, Flex_Battery_Interrupter.GBP, Flex_Battery_Interrupter.GBS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]
2021-04-21 Added the Flex Battery Interrupter 200 (200mm). Model:200,Version:1.01
    [Flex_Battery_Interrupter_200.kicad_pcb, Flex_Battery_Interrupter_200.sch]
2021-04-21 Updated readme file
    Added information to help makers build Flex Battery Interrupters.
2021-09-04 Added the assembly guide and 3D printed case design
    [Flex_Battery_Interrupter_BOM.csv, Flex_Battery_Interrupter_BOM.xlsx, Flex_Battery_Interrupter_BOM_v1.0.csv, Flex_Battery_Interrupter_BOM_v1.0.xlsx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]
2021-09-13 Updated files to match MMC Documentation template
    [Flex_Battery_Interrupter_100.brd, Flex_Battery_Interrupter_100.sch, Flex_Battery_Interrupter_200.kicad_pcb, Flex_Battery_Interrupter_200.sch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]
2021-09-13 Updated assembly Guide
2021-09-14 PCB Fabrication Documentation was added
2023-11-03 Add 3D Printing Files for Cable Tie Holder
    [Cable_Tie_Holder_Back.stl, Cable_Tie_Holder_Front.stl]
2023-11-03 Organize documentation folders
    [Flex_Battery_Interrupter_BOM.csv, Flex_Battery_Interrupter_BOM.xlsx, Flex_Battery_Interrupter_BOM_v1.0.xlsx, Flex_Battery_Interrupter_PCB_Cost.xlsx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]
2024-04-18 Added files for 3D printed tools
    [Assembly Tool Base.stl, Assembly Tool Top.stl, Removal Tool Base.stl, Removal Tool Pusher.stl]
2026-05-21 Added PCB Tester files
    [Flex PCB Tester.stl]
